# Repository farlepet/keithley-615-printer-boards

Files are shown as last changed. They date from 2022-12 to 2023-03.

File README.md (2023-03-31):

Keithley 615 Electrometer Printer Board Recreation
==================================================

This repo contains modern reproductions of the buffer/printer PCBs (PC209, PC218)
for the Keithley 615 electrometer.

Boards
------

 - PC218
   - Signal inverter/buffer board
   - Recreation of the origional PC218 schematic using modern SMD components is
     in the `PC218` directory
   - A simplified version using more modern ICs can be found in the `PC218v2` directory
 - PC209
   - Signal inverter/buffer and trigger board
   - Simplified version of the origional board can be found in the `PC209` directory
     - Same inverter/buffer scheme as PC218v2, with the origional trigger pulse
       generator and logic reduced down to discrete transistors, to simplify design.
 - Digital Interface Board
   - This will be a new board designed to connect to the 615 via the 50-pin
     Centronics connector
   - Planned features:
     - Passive data collection
     - Active triggering
     - USB-serial
     - RS-232 via DE-9
     - Ethernet

Photos
------

PC218 v2.2:
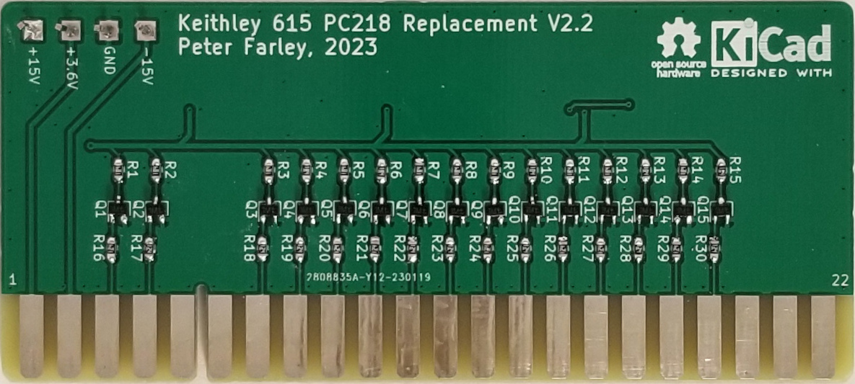
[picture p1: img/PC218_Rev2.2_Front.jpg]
Front of PC218 board v2.2

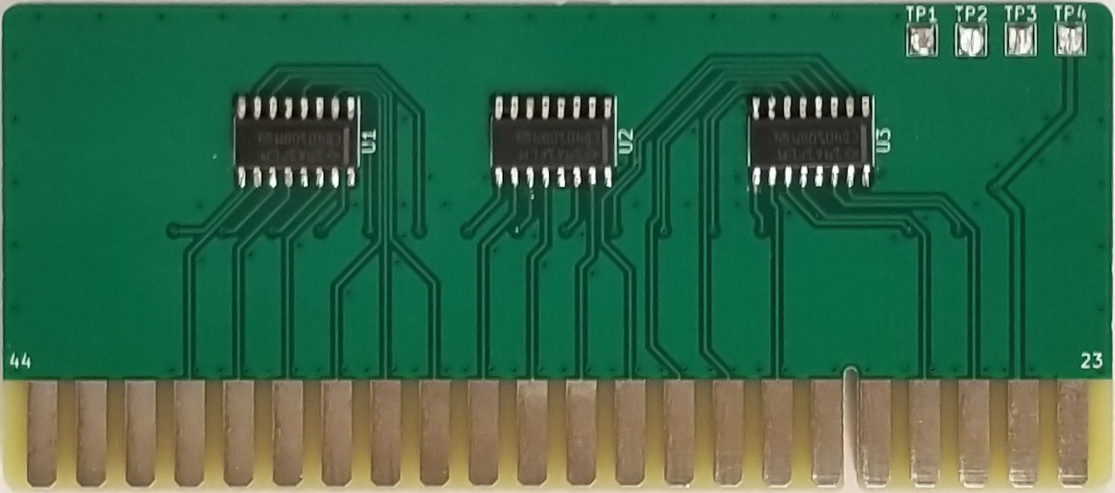
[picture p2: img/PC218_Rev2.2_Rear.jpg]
Rear of PC218 board v2.2


PC209 v1.0:
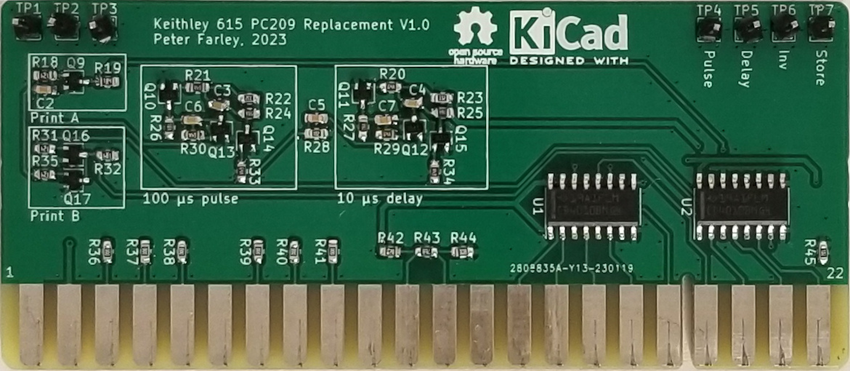
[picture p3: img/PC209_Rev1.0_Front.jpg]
Front of PC209 board v1.0

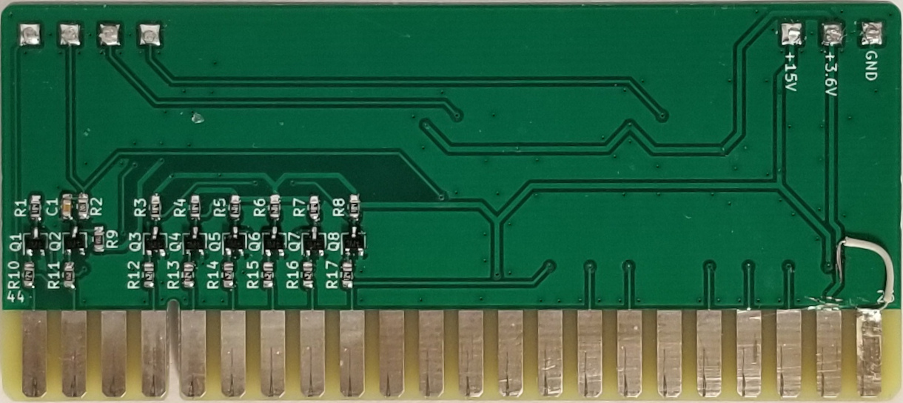
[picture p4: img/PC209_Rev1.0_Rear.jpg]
Rear of PC209 board v1.0


Interface/network board v1.0:
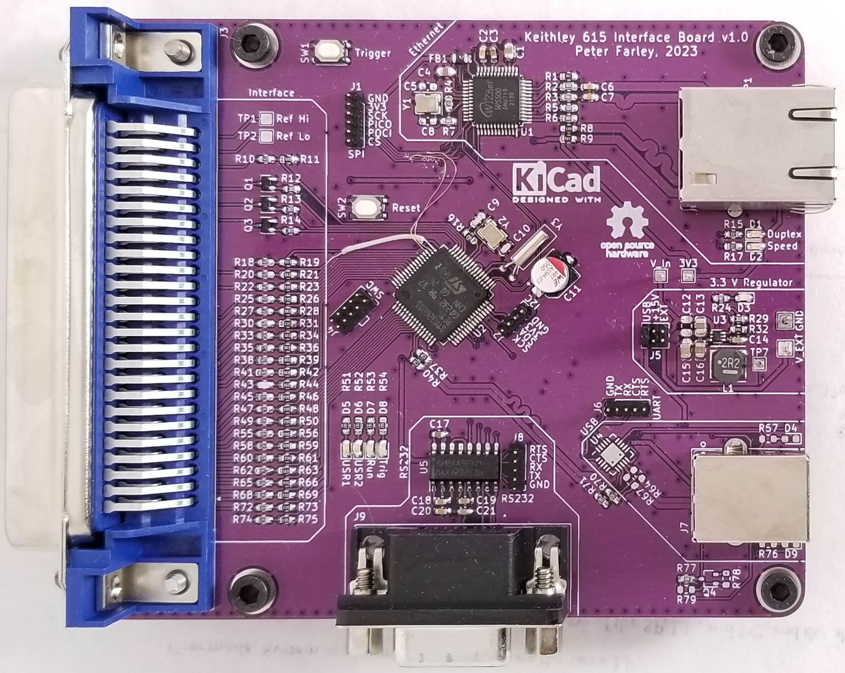
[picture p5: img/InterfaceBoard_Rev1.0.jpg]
Interface board v1.0


50-pin test board v1.0:
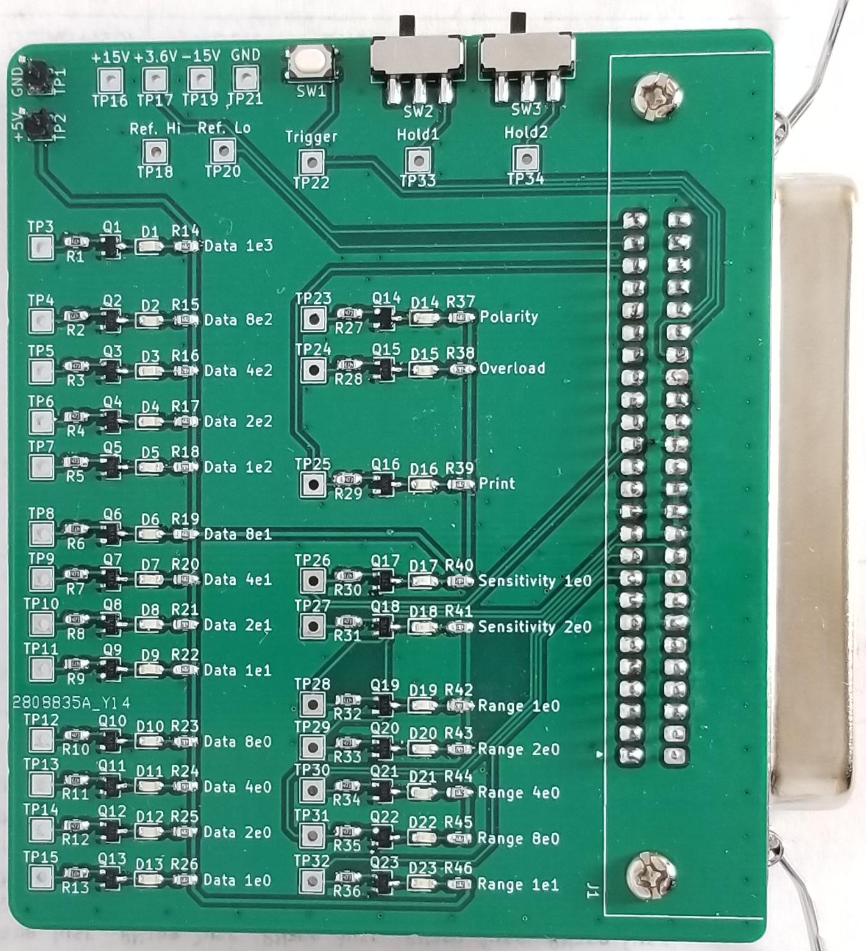
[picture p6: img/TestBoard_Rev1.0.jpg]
50-pin test board v1.0


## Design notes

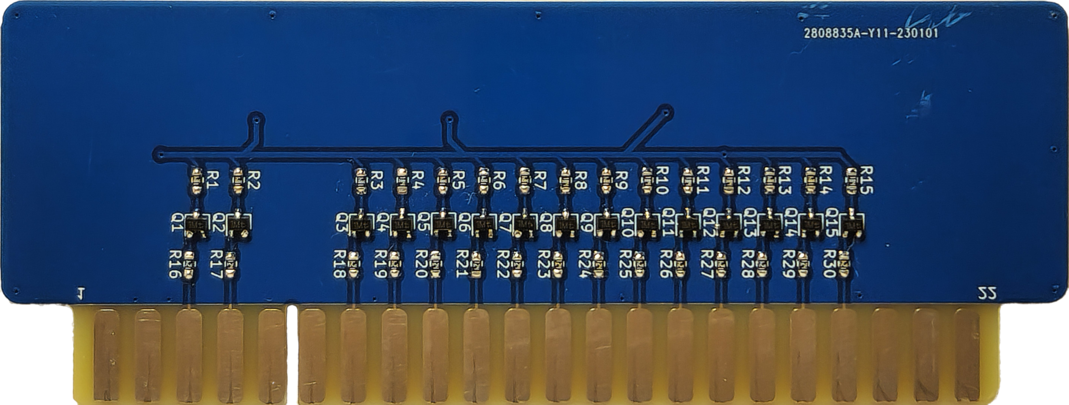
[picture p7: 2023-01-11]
img/PC218_Rev2.0_Front.png

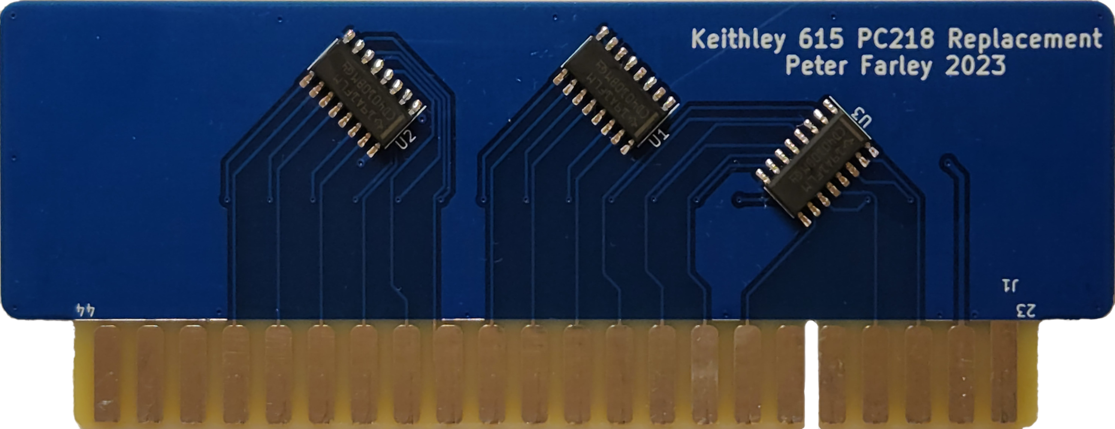
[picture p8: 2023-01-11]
img/PC218_Rev2.0_Rear.png

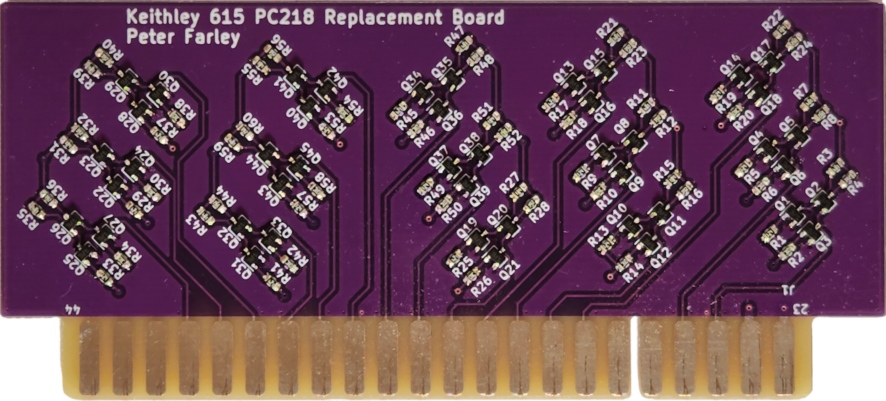
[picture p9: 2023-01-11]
img/PC218_Rev1.0.png

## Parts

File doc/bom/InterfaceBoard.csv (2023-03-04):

Source: | /home/farlepet/projects/electronics/test_equipment/keithley_615_printer_board/InterfaceBoard/InterfaceBoard.kicad_sch
Date: | Sat 04 Mar 2023 08:33:24 AM CST
Tool: | Eeschema (6.0.11)
Generator: | /usr/share/kicad/plugins/bom_csv_grouped_by_value.py
Component Count: | 163
Collated Components:
Item | Qty | Reference(s) | Value | LibPart | Footprint | Datasheet | DigiKey | MANUFACTURER | Model | PART_REV | STANDARD
1 | 4 | C1, C4, C12, C13 | 10uF | Device:C_Small | Capacitor_SMD:C_0805_2012Metric | https://media.digikey.com/pdf/Data%20Sheets/Samsung%20PDFs/CL21A106MQFNNNE_Spec.pdf | https://www.digikey.com/en/products/detail/samsung-electro-mechanics/CL21A106MQFNNNE/3886956
2 | 5 | C2, C5, C8, C36, C37 | 10nF | Device:C_Small | Capacitor_SMD:C_0603_1608Metric | ~ | https://www.digikey.com/en/products/detail/walsin-technology-corporation/0603B103K500CT/9354883
3 | 2 | C3, C35 | 4.7uF | Device:C_Small | Capacitor_SMD:C_0603_1608Metric | ~ | https://www.digikey.com/en/products/detail/samsung-electro-mechanics/CL10A475KQ8NNNC/3886703
4 | 3 | C6, C7, C29 | 6.8nF | Device:C_Small | Capacitor_SMD:C_0603_1608Metric | ~ | https://www.digikey.com/en/products/detail/walsin-technology-corporation/0603B683K160CT/9354958
5 | 2 | C9, C10 | 12pF | Device:C_Small | Capacitor_SMD:C_0603_1608Metric | http://www.passivecomponent.com/wp-content/uploads/datasheet/WTC_MLCC_General_Purpose.pdf | https://www.digikey.com/en/products/detail/walsin-technology-corporation/0603N120J500CT/9354977
6 | 1 | C11 | 4.7uF | Device:C_Polarized_Small | Capacitor_SMD:CP_Elec_5x5.9 | https://www.we-online.com/components/products/datasheet/865230642008.pdf | https://www.digikey.com/en/products/detail/w%C3%BCrth-elektronik/865230642008/5727868
7 | 15 | C14, C18, C19, C20, C21, C22, C23, C24, C25, C26, C27, C28, C32, C33, C34 | 100nF | Device:C_Small | Capacitor_SMD:C_0603_1608Metric | ~ | https://www.digikey.com/en/products/detail/samsung-electro-mechanics/CL10B104KB8NNWC/3887593
8 | 2 | C15, C16 | 22uF | Device:C_Small | Capacitor_SMD:C_0805_2012Metric | https://media.digikey.com/pdf/Data%20Sheets/Samsung%20PDFs/CL21A226MAYNNNE_Spec.pdf | https://www.digikey.com/en/products/detail/samsung-electro-mechanics/CL21A226MAYNNNE/10479857
9 | 1 | C17 | 1uF | Device:C_Small | Capacitor_SMD:C_0603_1608Metric | ~ | https://www.digikey.com/en/products/detail/samsung-electro-mechanics/CL10A105KA8NNNC/3886760
10 | 2 | C30, C31 | 22pF | Device:C_Small | Capacitor_SMD:C_0603_1608Metric | ~ | https://www.digikey.com/en/products/detail/walsin-technology-corporation/0603N220J500CT/9355000
11 | 2 | C38, C39 | 47pF | Device:C_Small | Capacitor_SMD:C_0603_1608Metric | ~ | https://www.digikey.com/en/products/detail/walsin-technology-corporation/0603N470J500CT/9355025
12 | 1 | D1 | Duplex | Device:LED_Small | LED_SMD:LED_0603_1608Metric | ~ | https://www.digikey.com/en/products/detail/harvatek-corporation/B1911USD-20D000114U1930/15519991
13 | 1 | D2 | Speed | Device:LED_Small | LED_SMD:LED_0603_1608Metric | ~ | https://www.digikey.com/en/products/detail/harvatek-corporation/B1911USD-20D000114U1930/15519991
14 | 7 | D3, D4, D5, D6, D7, D8, D9 | Red | Device:LED_Small | LED_SMD:LED_0603_1608Metric | ~ | https://www.digikey.com/en/products/detail/harvatek-corporation/B1911USD-20D000114U1930/15519991
15 | 3 | D10, D11, D12 | PE1605M1Q | Device:D_TVS | Diode_SMD:D_0402_1005Metric | https://www.panjit.com.tw/upload/datasheet/PE1605M1Q.pdf | https://www.digikey.com/en/products/detail/panjit-international-inc/PE1605M1Q-R1-00001/15798503
16 | 1 | FB1 | 1k | Device:FerriteBead_Small | Inductor_SMD:L_0805_2012Metric | https://abracon.com/Magnetics/new/ACML-0805.pdf | https://www.digikey.com/en/products/detail/abracon-llc/ACML-0805-102-T/4696707
17 | 1 | J3 | Keithley_50-Pin_Connector | lib_symbols:Keithley_50-Pin_Connector | lib:NorComp_112-050-213R001 |  | https://www.digikey.com/en/products/detail/norcomp-inc/112-050-213R001/955161
18 | 1 | J5 | Conn_02x03_Odd_Even | Connector_Generic:Conn_02x03_Odd_Even | Connector_PinHeader_1.27mm:PinHeader_2x03_P1.27mm_Vertical | ~
19 | 1 | J7 | USB_B | lib_symbols:UJ2-BH-W1-TH | lib:CUI_UJ2-BH-W1-TH | https://www.cuidevices.com/product/resource/uj2-bh-th.pdf | https://www.digikey.com/en/products/detail/cui-devices/UJ2-BH-W1-TH/6188082 | CUI INC |  | 1.0 | MANUFACTURER RECOMENDATION
20 | 1 | J9 | DB9_Female_MountingHoles | Connector:DB9_Female_MountingHoles | lib:ASSMANN_A-DF_09_A_KG-T2S | http://www.assmann-wsw.com/uploads/datasheets/ASS_4888_CO.pdf | https://www.digikey.com/en/products/detail/assmann-wsw-components/A-DF-09-A-KG-T2S/1241800
21 | 1 | L1 | 2.2 uH | Device:L_Small | Inductor_SMD:L_Taiyo-Yuden_NR-50xx | https://media.digikey.com/pdf/Data%20Sheets/Taiyo%20Yuden%20PDFs%20URL%20links/NRS5024T2R2NMGJ_SS.pdf | https://www.digikey.com/en/products/detail/taiyo-yuden/NRS5024T2R2NMGJ/4970841
22 | 1 | P1 | RB1-125BAG1A | lib_symbols:RB1-125BAG1A | lib:WIZNET_RB1-125BAG1A |  | https://www.digikey.com/en/products/detail/wiznet/RB1-125BAG1A/3829637 | WIZnet
23 | 3 | Q1, Q2, Q3 | BC848W | Transistor_BJT:BC848W | Package_TO_SOT_SMD:SOT-323_SC-70 | http://www.infineon.com/dgdl/Infineon-BC847SERIES_BC848SERIES_BC849SERIES_BC850SERIES-DS-v01_01-en.pdf?fileId=db3a304314dca389011541d4630a1657
24 | 1 | Q4 | BC856W | Transistor_BJT:BC856W | Package_TO_SOT_SMD:SOT-323_SC-70 | https://www.onsemi.com/pub/Collateral/BC860-D.pdf
25 | 1 | R1 | 12.4k | Device:R_Small | Resistor_SMD:R_0603_1608Metric | ~ | https://www.digikey.com/en/products/detail/stackpole-electronics-inc/RMCF0603FT12K4/1761222
26 | 13 | R2, R3, R5, R6, R7, R70, R71, R77, R80, R86, R87, R90, R91 | 0 | Device:R_Small | Resistor_SMD:R_0603_1608Metric | ~ | https://www.digikey.com/en/products/detail/walsin-technology-corporation/WR06X000-PTL/5978108
27 | 1 | R4 | 1M | Device:R_Small | Resistor_SMD:R_0603_1608Metric | ~ | https://www.digikey.com/en/products/detail/walsin-technology-corporation/WR06X105-JTL/13239221
28 | 4 | R8, R9, R82, R83 | 49.9 | Device:R_Small | Resistor_SMD:R_0603_1608Metric | ~ | https://www.digikey.com/en/products/detail/stackpole-electronics-inc/RMCF0603FT49R9/1760879
29 | 23 | R10, R18, R20, R22, R25, R27, R30, R33, R35, R38, R41, R43, R45, R47, R49, R55, R58, R60, R62, R65, R68, R72, R74 | 220k | Device:R_Small | Resistor_SMD:R_0603_1608Metric | ~ | https://www.digikey.com/en/products/detail/walsin-technology-corporation/WR06X224-JTL/13238727
30 | 23 | R11, R19, R21, R23, R26, R28, R31, R34, R36, R39, R42, R44, R46, R48, R50, R56, R59, R61, R63, R66, R69, R73, R75 | 56k | Device:R_Small | Resistor_SMD:R_0603_1608Metric | ~ | https://www.digikey.com/en/products/detail/stackpole-electronics-inc/RMCF0603JT56K0/1757988
31 | 5 | R12, R13, R14, R29, R79 | 10k | Device:R_Small | Resistor_SMD:R_0603_1608Metric | ~ | https://www.digikey.com/en/products/detail/yageo/RC0603FR-1010KL/12756395
32 | 4 | R15, R17, R81, R84 | 330 | Device:R_Small | Resistor_SMD:R_0603_1608Metric | ~ | https://www.digikey.com/en/products/detail/walsin-technology-corporation/WR06X331-JTL/13240667
33 | 1 | R16 | 1.6k | Device:R_Small | Resistor_SMD:R_0603_1608Metric | ~ | https://www.digikey.com/en/products/detail/stackpole-electronics-inc/RMCF0603FT1K60/1761204
34 | 3 | R24, R57, R76 | 1k | Device:R_Small | Resistor_SMD:R_0603_1608Metric | ~ | https://www.digikey.com/en/products/detail/walsin-technology-corporation/WR06X102-JTL/13241138
35 | 1 | R32 | 31.6k | Device:R_Small | Resistor_SMD:R_0603_1608Metric | ~ | https://www.digikey.com/en/products/detail/bourns-inc/CR0603-FX-3162ELF/3783940
36 | 4 | R37, R40, R64, R67 | 27 | Device:R_Small | Resistor_SMD:R_0603_1608Metric | ~ | https://www.digikey.com/en/products/detail/stackpole-electronics-inc/RMCF0603FT27R0/1760818
37 | 4 | R51, R52, R53, R54 | 1.8k | Device:R_Small | Resistor_SMD:R_0603_1608Metric | ~ | https://www.digikey.com/en/products/detail/stackpole-electronics-inc/RMCF0603JG1K80/1712125
38 | 1 | R78 | 180k | Device:R_Small | Resistor_SMD:R_0603_1608Metric | ~ | https://www.digikey.com/en/products/detail/yageo/RC0603FR-10180KL/14008354
39 | 1 | R85 | 10 | Device:R_Small | Resistor_SMD:R_0603_1608Metric | ~ | https://www.digikey.com/en/products/detail/walsin-technology-corporation/WR06X10R0FTL/13238870
40 | 2 | R88, R89 | 1.5k | Device:R_Small | Resistor_SMD:R_0603_1608Metric | ~ | https://www.digikey.com/en/products/detail/walsin-technology-corporation/WR06X1501FTL/13239261
41 | 2 | SW1, SW2 | PTS810 | Switch:SW_Push | Button_Switch_SMD:SW_SPST_PTS810 | ~ | https://www.digikey.com/en/products/detail/c-k/PTS810-SJK-250-SMTR-LFS/4176611
42 | 1 | U1 | W5500 | Interface_Ethernet:W5500 | Package_QFP:LQFP-48_7x7mm_P0.5mm | http://wizwiki.net/wiki/lib/exe/fetch.php/products:w5500:w5500_ds_v109e.pdf | https://www.digikey.com/en/products/detail/wiznet/W5500/4425702
43 | 1 | U2 | STM32G0B1RET | lib_symbols:STM32G0B1RET | Package_QFP:LQFP-64_10x10mm_P0.5mm |  | https://www.digikey.com/en/products/detail/stmicroelectronics/STM32G0B1RET6/13693663
44 | 1 | U3 | AP62250Z6 | Regulator_Switching:AP62250Z6 | Package_TO_SOT_SMD:SOT-563 | https://www.diodes.com/assets/Datasheets/AP62250.pdf | https://www.digikey.com/en/products/detail/diodes-incorporated/AP62250Z6-7/12349310
45 | 1 | U4 | FT231XQ | Interface_USB:FT231XQ | Package_DFN_QFN:QFN-20-1EP_4x4mm_P0.5mm_EP2.5x2.5mm | https://www.ftdichip.com/Support/Documents/DataSheets/ICs/DS_FT231X.pdf | https://www.digikey.com/en/products/detail/ftdi-future-technology-devices-international-ltd/FT231XQ-T/3749470
46 | 1 | U5 | MAX3232 | Interface_UART:MAX3232 | Package_SO:SOIC-16_3.9x9.9mm_P1.27mm | https://www.ti.com/lit/ds/symlink/max3232e.pdf | https://www.digikey.com/en/products/detail/texas-instruments/MAX3232EIDR/1089416?s=N4IgTCBcDaILYEMDGBmMaQF0C%2BQ
47 | 1 | Y1 | 25 MHz | Device:Crystal_GND24 | Crystal:Crystal_SMD_3225-4Pin_3.2x2.5mm | ~ | https://www.digikey.com/en/products/detail/raltron-electronics/RH100-25-000-18-F-TR/15963302 |  | RH100-25.000-18-F-TR
48 | 1 | Y2 | 24 MHz | Device:Crystal_GND24_Small | Crystal:Crystal_SMD_3225-4Pin_3.2x2.5mm | https://www.raltron.com/webproducts/specs/CRYSTAL/RH100-24.000-12-1010-EXT-TR.pdf | https://www.digikey.com/en/products/detail/raltron-electronics/RH100-24-000-12-1010-EXT-TR/15963325
49 | 1 | Y3 | 32.768 kHz | Device:Crystal_Small | Crystal:Crystal_C26-LF_D2.1mm_L6.5mm_Horizontal | https://www.yic.com.tw/wp-content/uploads/2019/05/YIC-DT38-DT26-DT15.pdf | https://www.digikey.com/en/products/detail/yic/32-768K12-5P2-DT26/15648604

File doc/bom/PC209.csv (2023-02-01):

Source: | /home/farlepet/projects/electronics/test_equipment/keithley_615_printer_board/PC209/PC209.kicad_sch
Date: | Wed 01 Feb 2023 06:48:42 AM CST
Tool: | Eeschema (6.0.11)
Generator: | /usr/share/kicad/plugins/bom_csv_grouped_by_value.py
Component Count: | 72
Collated Components:
Item | Qty | Reference(s) | Value | LibPart | Footprint | Datasheet | Digikey
1 | 2 | C1, C5 | 1 nF | Device:C_Small | Capacitor_SMD:C_0603_1608Metric | ~ | https://www.digikey.com/en/products/detail/walsin-technology-corporation/0603B102K500CT/9354877
2 | 1 | C2 | 100 pF | Device:C_Small | Capacitor_SMD:C_0603_1608Metric | ~ | https://www.digikey.com/en/products/detail/walsin-technology-corporation/0603B101K500CT/14836835
3 | 1 | C3 | 100 nF | Device:C_Small | Capacitor_SMD:C_0603_1608Metric | ~ | https://www.digikey.com/en/products/detail/samsung-electro-mechanics/CL10B104KB8NNWC/3887593
4 | 1 | C4 | 3.3 nF | Device:C_Small | Capacitor_SMD:C_0603_1608Metric | ~ | https://www.digikey.com/en/products/detail/samsung-electro-mechanics/CL10B332KB8NNNC/3887416
5 | 2 | C6, C7 | 470 pF | Device:C_Small | Capacitor_SMD:C_0603_1608Metric | ~ | https://www.digikey.com/en/products/detail/samsung-electro-mechanics/CL10B471KB8NNNC/3886752
6 | 1 | J1 | PC209_BoardEdge_44pin | lib_symbols:PC209_BoardEdge_44pin | footprints:PC209_Edge_Connector
7 | 17 | Q1, Q2, Q3, Q4, Q5, Q6, Q7, Q8, Q9, Q10, Q11, Q12, Q13, Q14, Q15, Q16, Q17 | BC848W | Transistor_BJT:BC848W | Package_TO_SOT_SMD:SOT-323_SC-70 | http://www.infineon.com/dgdl/Infineon-BC847SERIES_BC848SERIES_BC849SERIES_BC850SERIES-DS-v01_01-en.pdf?fileId=db3a304314dca389011541d4630a1657 | https://www.digikey.com/en/products/detail/nexperia-usa-inc/BC848W-115/1232299
8 | 9 | R1, R3, R4, R5, R6, R7, R8, R19, R32 | 180k | Device:R_Small | Resistor_SMD:R_0603_1608Metric | ~ | https://www.digikey.com/en/products/detail/yageo/RC0603FR-10180KL/14008354
9 | 3 | R2, R28, R45 | 1k | Device:R_Small | Resistor_SMD:R_0603_1608Metric | ~ | https://www.digikey.com/en/products/detail/walsin-technology-corporation/WR06X102-JTL/13241138
10 | 5 | R9, R24, R25, R26, R27 | 634 | Device:R_Small | Resistor_SMD:R_0603_1608Metric | ~ | https://www.digikey.com/en/products/detail/stackpole-electronics-inc/RMCF0603FT634R/1760903
11 | 10 | R10, R12, R13, R14, R15, R16, R17, R18, R31, R35 | 120k | Device:R_Small | Resistor_SMD:R_0603_1608Metric | ~ | https://www.digikey.com/en/products/detail/yageo/RC0603FR-13120KL/14008276
12 | 7 | R11, R20, R21, R29, R30, R33, R34 | 453 | Device:R_Small | Resistor_SMD:R_0603_1608Metric | ~ | https://www.digikey.com/en/products/detail/stackpole-electronics-inc/RMCF0603FT453R/1714054
13 | 2 | R22, R23 | 3.3k | Device:R_Small | Resistor_SMD:R_0603_1608Metric | ~ | https://www.digikey.com/en/products/detail/walsin-technology-corporation/WR06X3301FTL/13239039
14 | 6 | R36, R37, R38, R39, R40, R41 | 0 | Device:R_Small | Resistor_SMD:R_0603_1608Metric | ~ | https://www.digikey.com/en/products/detail/walsin-technology-corporation/WR06X000-PTL/5978108
15 | 1 | R42 | 6.98k | Device:R | Resistor_SMD:R_0603_1608Metric | ~ | https://www.digikey.com/en/products/detail/yageo/RC0603FR-076K98L/727326
16 | 1 | R43 | 6.04k | Device:R | Resistor_SMD:R_0603_1608Metric | ~ | https://www.digikey.com/en/products/detail/yageo/RC0603FR-076K04L/727317
17 | 1 | R44 | 2k | Device:R | Resistor_SMD:R_0603_1608Metric | ~ | https://www.digikey.com/en/products/detail/yageo/RC0603FR-072KL/727009
18 | 2 | U1, U2 | 4010 | 4xxx:4010 | Package_SO:SOIC-16_3.9x9.9mm_P1.27mm | http://www.ti.com/lit/ds/symlink/cd4010b-q1.pdf | https://www.digikey.com/en/products/detail/texas-instruments/CD4010BM96/1690674

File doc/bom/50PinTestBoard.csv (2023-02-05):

Source: | /home/farlepet/projects/electronics/test_equipment/keithley_615_printer_board/50PinTestBoard/50PinTestBoard.kicad_sch
Date: | Sat 04 Feb 2023 09:08:30 PM CST
Tool: | Eeschema (6.0.11)
Generator: | /usr/share/kicad/plugins/bom_csv_grouped_by_value.py
Component Count: | 98
Item | Qty | Reference(s) | Value | LibPart | Footprint | Datasheet | DigiKey
1 | 23 | D1, D2, D3, D4, D5, D6, D7, D8, D9, D10, D11, D12, D13, D14, D15, D16, D17, D18, D19, D20, D21, D22, D23 | LED | Device:LED | LED_SMD:LED_0603_1608Metric | ~ | https://www.digikey.com/en/products/detail/harvatek-corporation/B1911NG-20D000214U1930/15519989
2 | 1 | J1 | Keithley_50-Pin_Connector | lib_symbols:Keithley_50-Pin_Connector | footprints:NorComp_112-050-213R001 |  | https://www.digikey.com/en/products/detail/norcomp-inc/112-050-213R001/955161
3 | 23 | Q1, Q2, Q3, Q4, Q5, Q6, Q7, Q8, Q9, Q10, Q11, Q12, Q13, Q14, Q15, Q16, Q17, Q18, Q19, Q20, Q21, Q22, Q23 | BC848W | Transistor_BJT:BC848W | Package_TO_SOT_SMD:SOT-323_SC-70 | http://www.infineon.com/dgdl/Infineon-BC847SERIES_BC848SERIES_BC849SERIES_BC850SERIES-DS-v01_01-en.pdf?fileId=db3a304314dca389011541d4630a1657 | https://www.digikey.com/en/products/detail/nexperia-usa-inc/BC848W-115/1232299
4 | 23 | R1, R2, R3, R4, R5, R6, R7, R8, R9, R10, R11, R12, R13, R27, R28, R29, R30, R31, R32, R33, R34, R35, R36 | 50k | Device:R_Small | Resistor_SMD:R_0603_1608Metric | ~ | https://www.digikey.com/en/products/detail/walsin-technology-corporation/WR06X473-JTL/13240660
5 | 23 | R14, R15, R16, R17, R18, R19, R20, R21, R22, R23, R24, R25, R26, R37, R38, R39, R40, R41, R42, R43, R44, R45, R46 | 6.8k | Device:R_Small | Resistor_SMD:R_0603_1608Metric | ~ | https://www.digikey.com/en/products/detail/walsin-technology-corporation/WR06X682-JTL/13240888
6 | 2 | R47, R48 | 0 | Device:R_Small | Resistor_SMD:R_0603_1608Metric | ~ | https://www.digikey.com/en/products/detail/walsin-technology-corporation/WR06X000-PTL/5978108
7 | 1 | SW1 | SW_Push | Switch:SW_Push | Button_Switch_SMD:SW_SPST_PTS810 | ~ | https://www.digikey.com/en/products/detail/c-k/PTS810-SJK-250-SMTR-LFS/4176611
8 | 2 | SW2, SW3 | SW_SPST | Switch:SW_SPST | Button_Switch_SMD:SW_SPDT_CK-JS102011SAQN | ~ | https://www.digikey.com/en/products/detail/c-k/JS102011SAQN/1640095

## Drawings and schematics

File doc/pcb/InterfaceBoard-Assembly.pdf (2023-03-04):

1 | 2 | 3 | 4 | 5 | 6

A

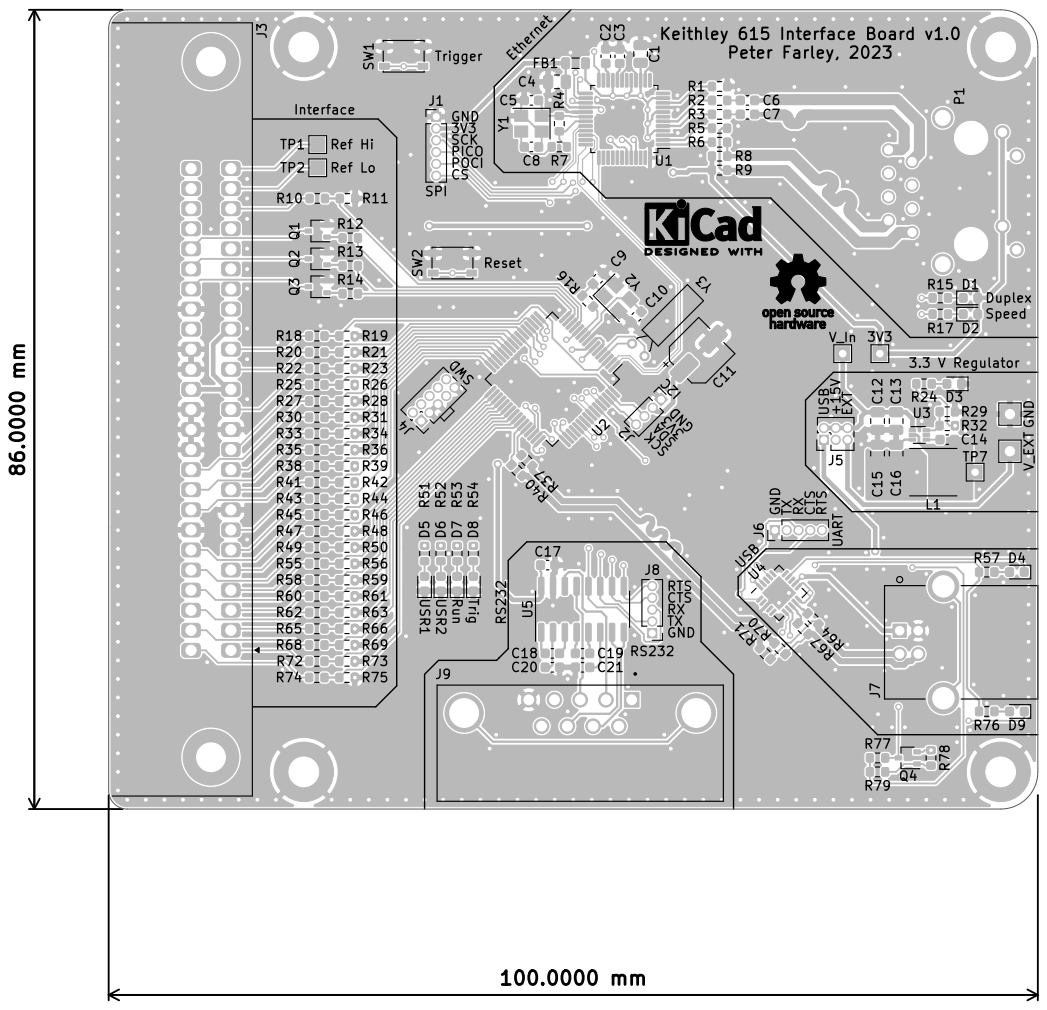
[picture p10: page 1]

Id: 1/1 Title: Keithley 615 Interface Board

1 | 2 | 3 | 4 | 5 | 6

A

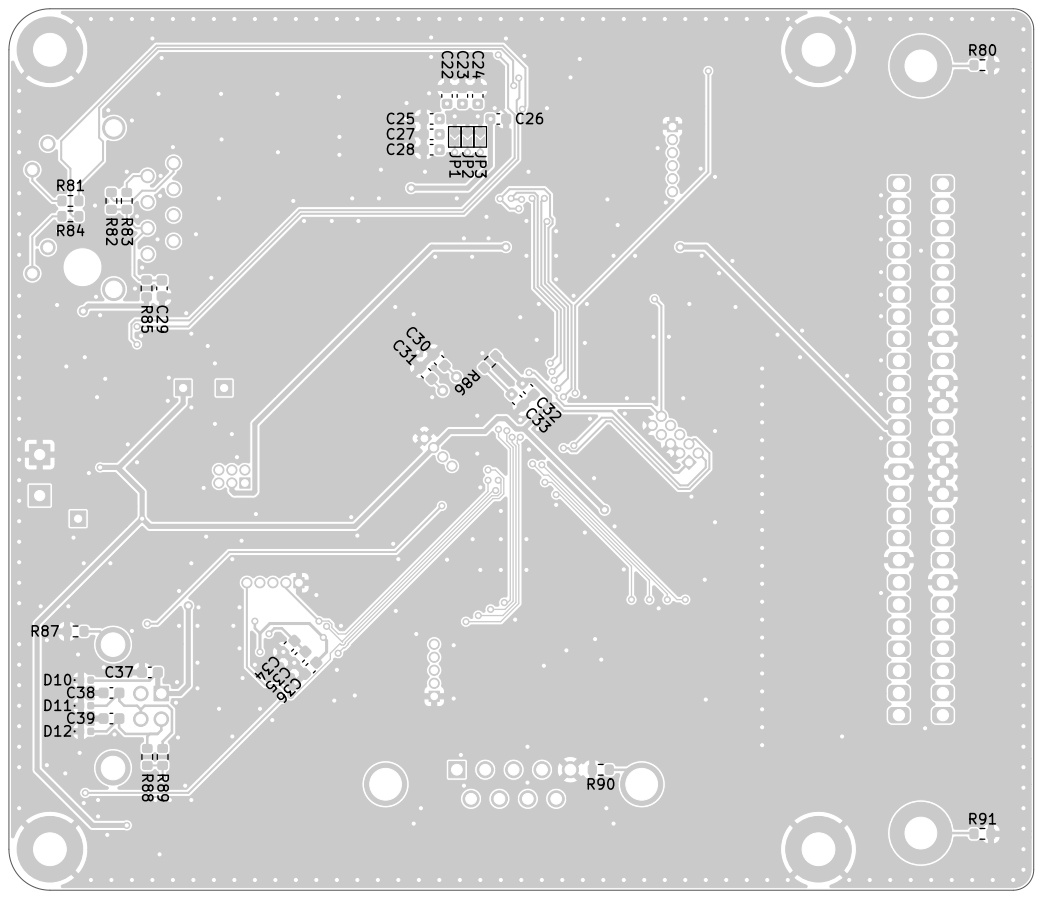
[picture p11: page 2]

Id: 1/1 Title: Keithley 615 Interface Board

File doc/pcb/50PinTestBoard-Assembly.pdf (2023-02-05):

1 | 2 | 3

A

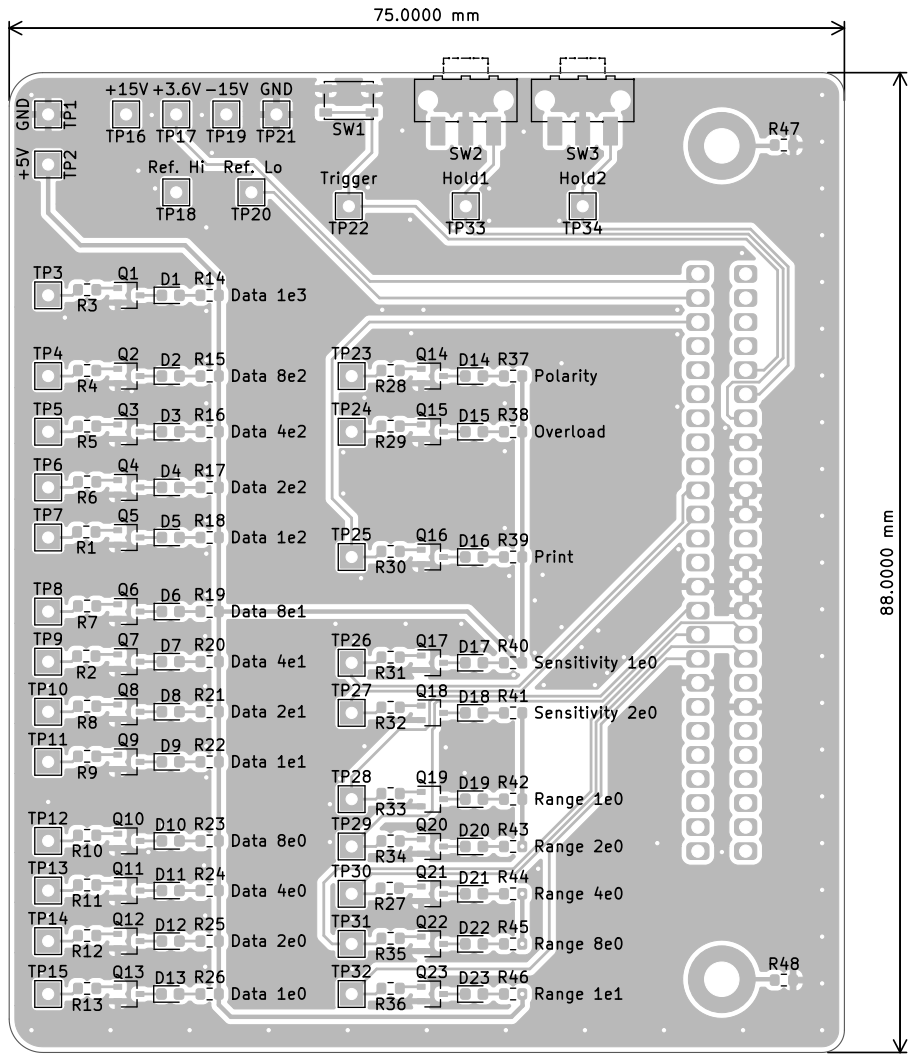
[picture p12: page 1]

1 | 2 | 3

A

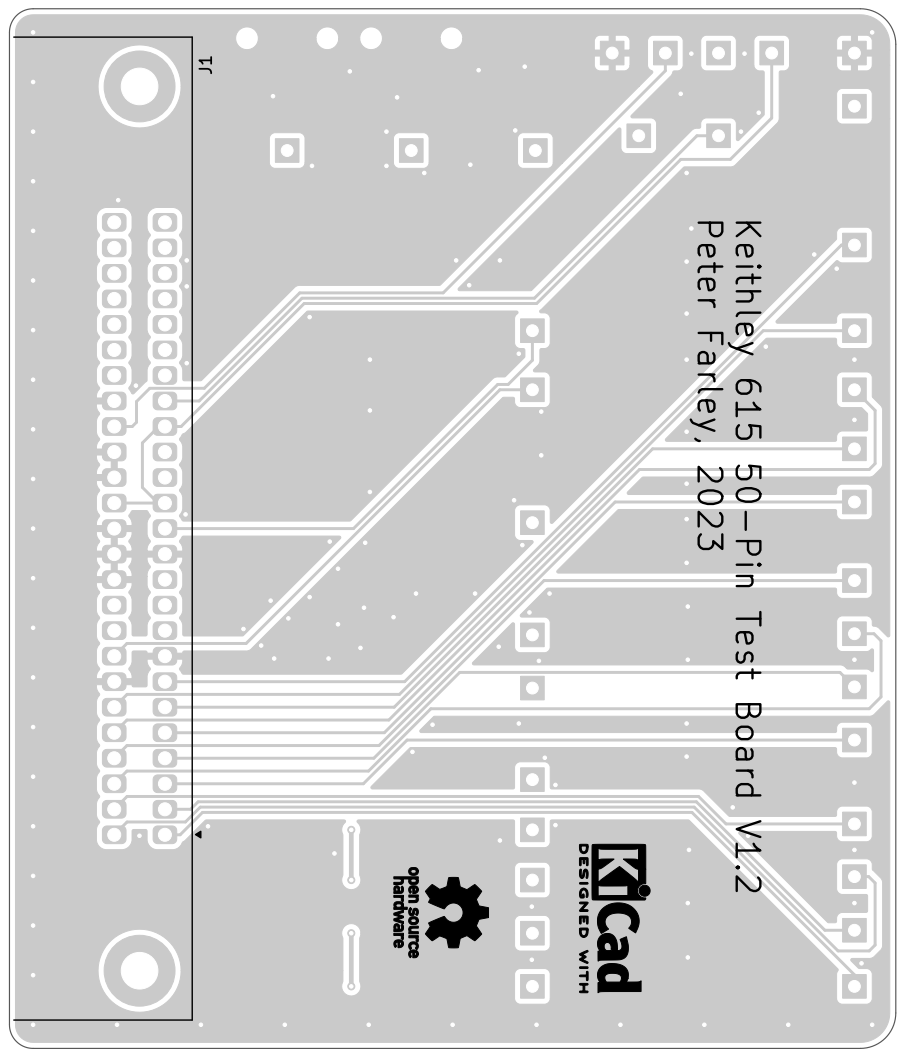
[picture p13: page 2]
D Date: 2023-02-04 KiCad; kicad; (6.0.11) Size: A5; Rev: 1.2; Id: 1/1 Title: Keithley 615 50-Pin; Test Board; Peter Farley Rev 1.0:; Initial Design Rev 1.1: Update connector; footprint Rev1.2:; Fix connector; orientation/pin; numbering; Keithley 615 50-Pin Test Board V1.2 Peter Farley, 2023 J1

File: 50PinTestBoard.kicad_pcb Sheet: BlackAndWhiteBottom

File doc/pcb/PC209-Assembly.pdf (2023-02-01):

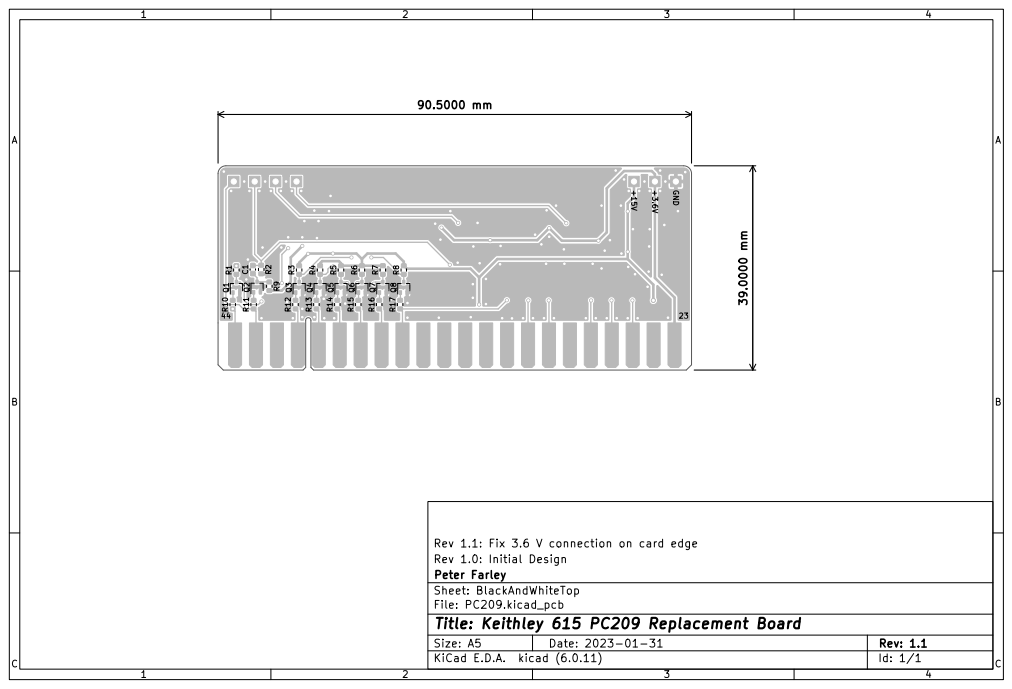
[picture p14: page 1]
BC Date: 2023-01-31 KiCad; kicad; (6.0.11) Size: A5; Rev: 1.1; File: PC209.kicad_pcb Sheet: BlackAndWhiteTop Peter; Farley Rev 1.0:; Initial Design Rev 1.1:; Fix 3.6 V connection; on card edge ⁺¹⁵V; GND R²; R¹²; R¹³ R⁹; R⁴ R¹¹; R¹⁴; R⁸ Q⁷ R¹⁵ Q²; R⁵ R¹⁰; R¹⁷ C¹; R¹⁶ R¹

Id: 1/1 Title: Keithley 615 PC209 Replacement Board

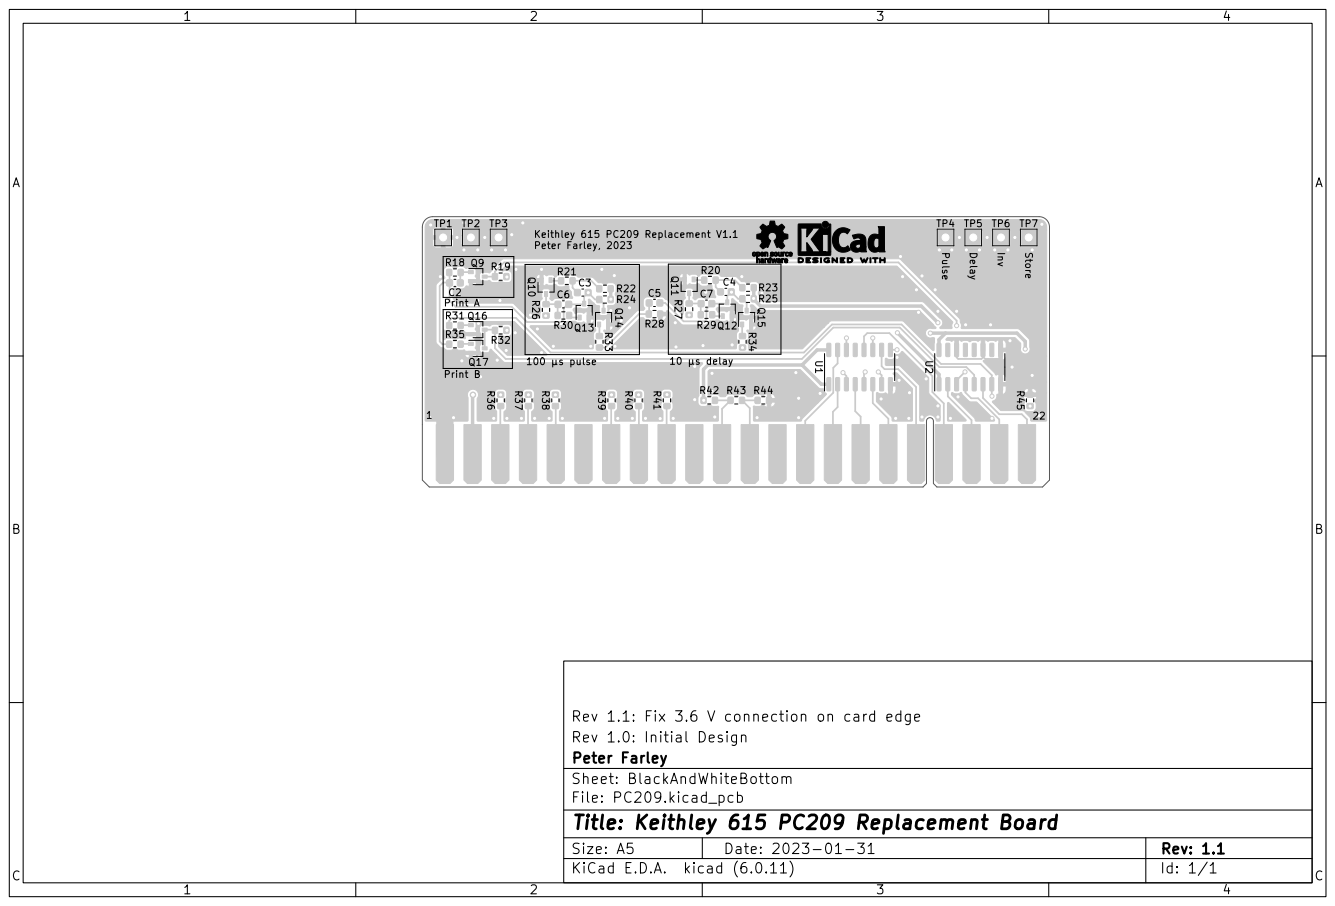
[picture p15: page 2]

Keithley 615 PC209 Replacement V1.1 Peter Farley, 2023

File: PC209.kicad_pcb Sheet: BlackAndWhiteBottom
Id: 1/1 Title: Keithley 615 PC209 Replacement Board

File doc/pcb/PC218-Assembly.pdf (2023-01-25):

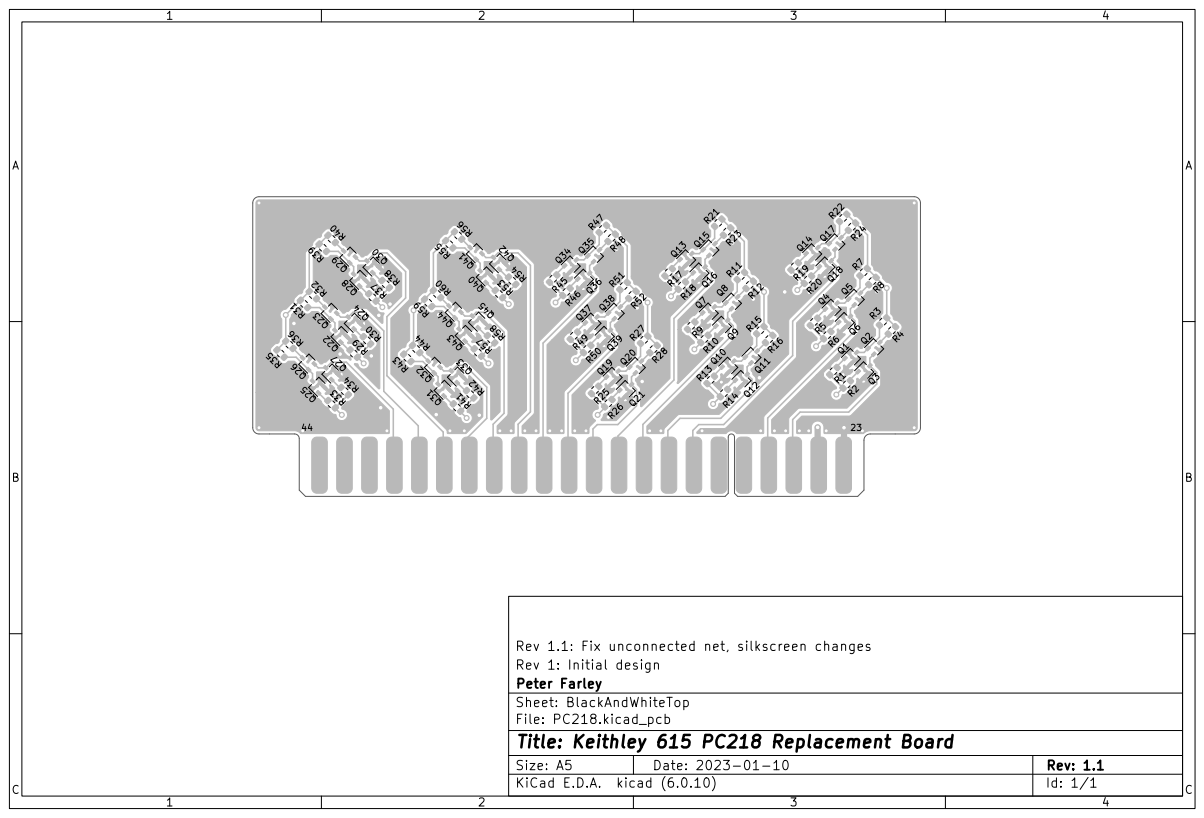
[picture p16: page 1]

Rev 1.1: Fix unconnected net, silkscreen changes
Rev 1: Initial design
Peter Farley
Sheet: BlackAndWhiteTop
File: PC218.kicad_pcb
Id: 1/1 Title: Keithley 615 PC218 Replacement Board

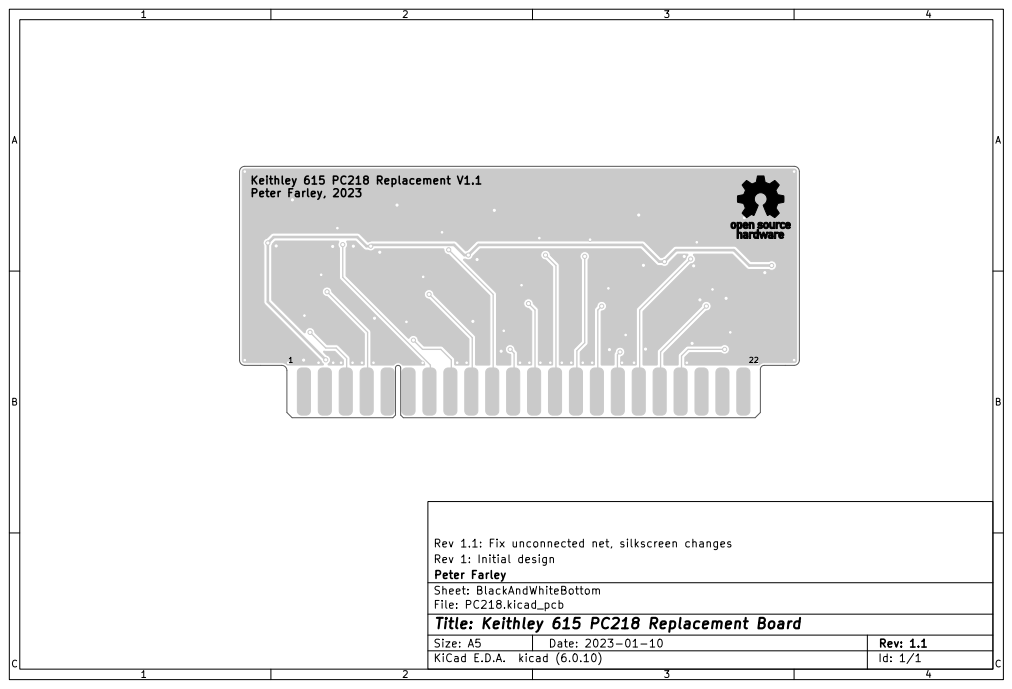
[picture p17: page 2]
BC Date: 2023-01-10 KiCad E.D.A. kicad (6.0.10) Size: A5; Rev: 1.1; Keithley 615 PC218 Replacement V1.1 Peter Farley, 2023

Rev 1.1: Fix unconnected net, silkscreen changes
Rev 1: Initial design
Peter Farley
File: PC218.kicad_pcb Sheet: BlackAndWhiteBottom
Id: 1/1 Title: Keithley 615 PC218 Replacement Board

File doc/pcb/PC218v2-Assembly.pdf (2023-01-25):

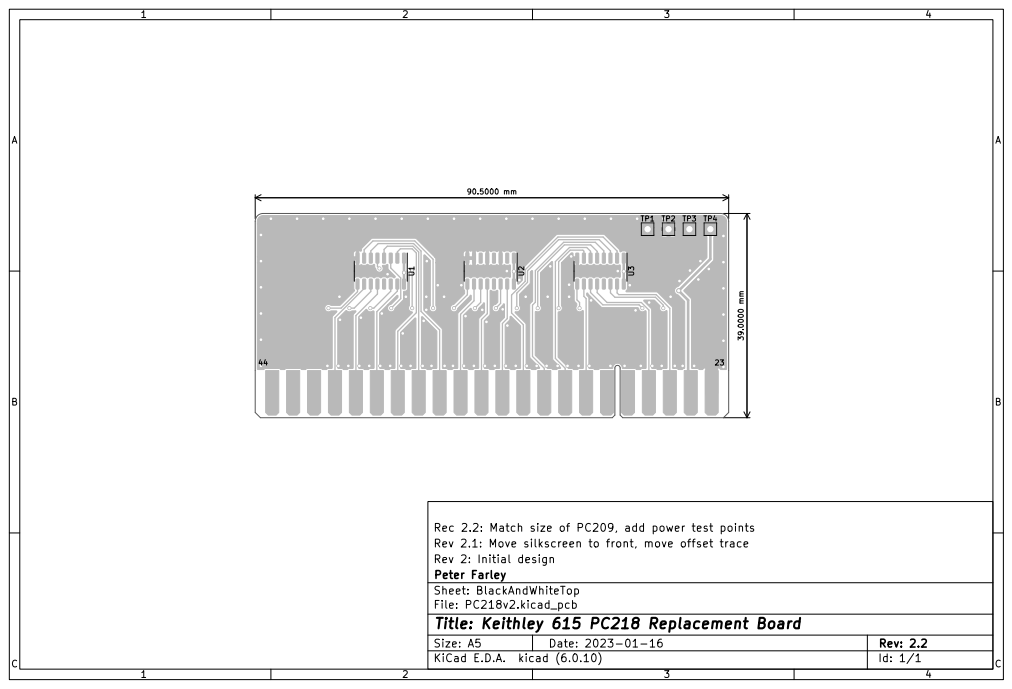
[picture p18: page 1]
BC Date: 2023-01-16 KiCad E.D.A. kicad (6.0.10) Size: A5; Rev: 2.2

Rec 2.2: Match size of PC209, add power test points
Rev 2.1: Move silkscreen to front, move offset trace
Rev 2: Initial design
Peter Farley
Sheet: BlackAndWhiteTop
File: PC218v2.kicad_pcb
Id: 1/1 Title: Keithley 615 PC218 Replacement Board

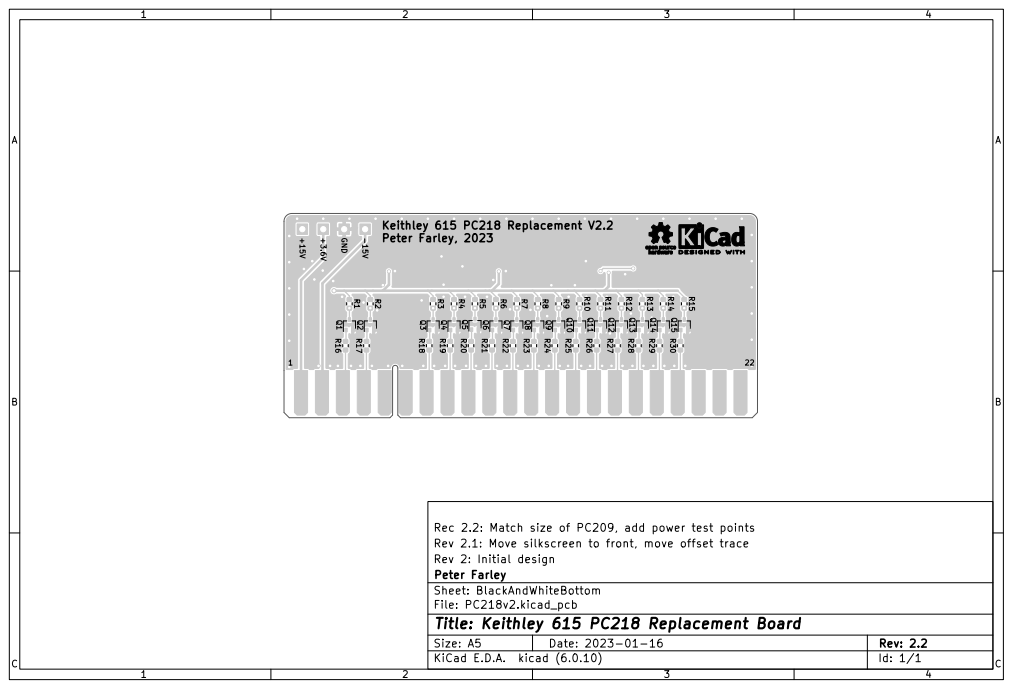
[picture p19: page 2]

Rev 2.1: Move silkscreen to front, move offset trace
Rev 2: Initial design
Peter Farley
File: PC218v2.kicad_pcb Sheet: BlackAndWhiteBottom
Id: 1/1 Title: Keithley 615 PC218 Replacement Board

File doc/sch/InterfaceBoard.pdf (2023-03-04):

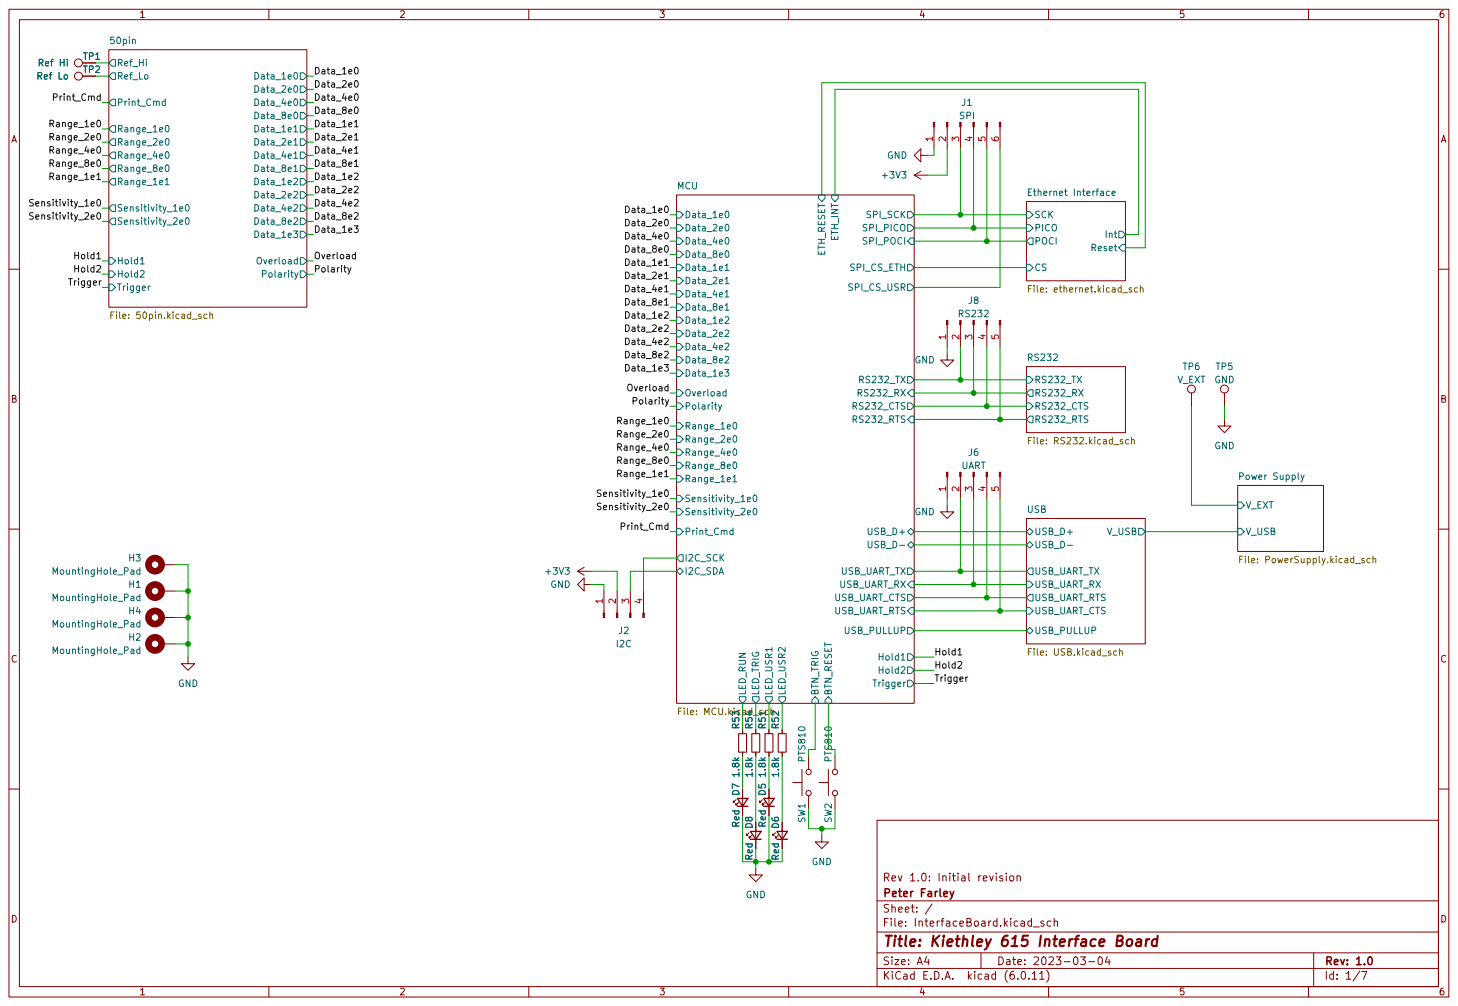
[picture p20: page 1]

Power Supply File: PowerSupply.kicad_sch SPI_PICO
SPI_POCI SPI_CS_ETH

Id: 1/7 Title: Kiethley 615 Interface Board

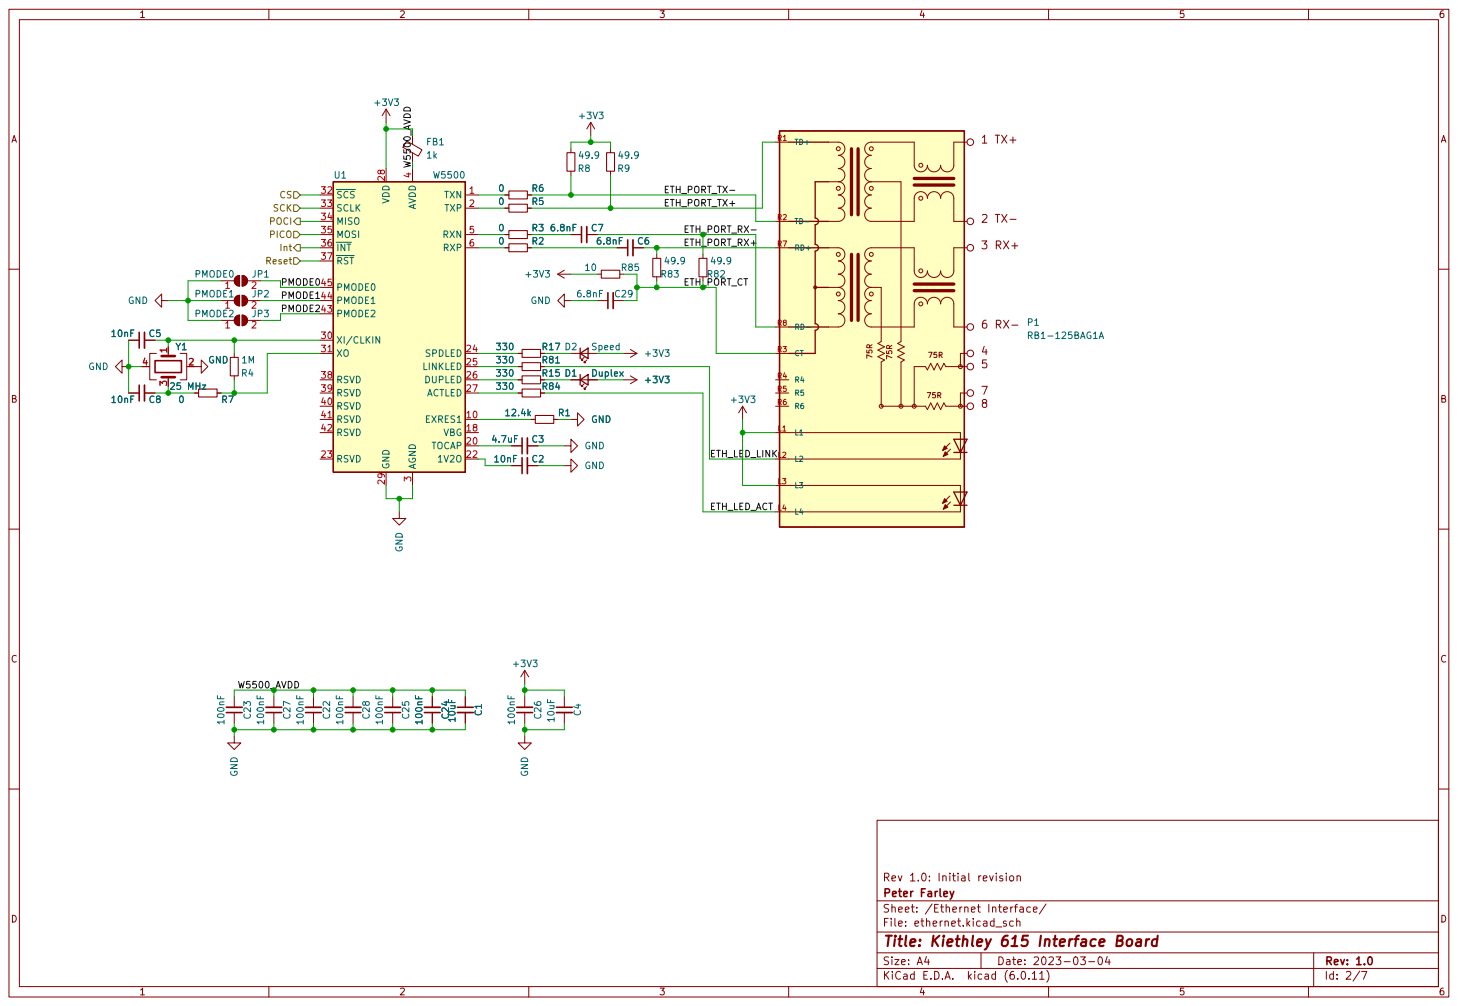
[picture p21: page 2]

4 RSVD 40 RSVD 41 RSVD 42 PMODE2 43 PMODE1 44 PMODE0 45 RXN

3 XI/CLKIN 30 XO 31 ~{SCS} 32 SCLK 33 MISO 34 MOSI 35 ~{INT} 36 ~{RST} 37 RSVD 38 RSVD 39 AVDD

L2
L2 L3 L3

Id: 2/7 Title: Kiethley 615 Interface Board


Id: 3/7 Title: Kiethley 615 Interface Board


17 ~{DTR}18 ~{RTS}19 ~{RI}2 VCCIO 20 GND 21 GND

FTDI USB UART Only populate one DNP for FTDI

3 ~{DSR}4 ~{DCD}5 ~{CTS}6 CBUS2 7 USBDP 8 USBDM 9 U4 FT231XQ D9 Red R76 1k R57 1k

3 GND
4 SHIELD

Id: 4/7 Title: Kiethley 615 Interface Board


Id: 5/7 Title: Kiethley 615 Interface Board


Id: 6/7 Title: Kiethley 615 Interface Board


Input cap current requirements: 5 V: ~150 mA

Id: 7/7 Title: Kiethley 615 Interface Board

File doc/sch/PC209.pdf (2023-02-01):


Hold 2 Out Range Hold Out Hold 1 Out Zero Check Out Buffer Storage

Range Hold Range Signal 8 V

Low Reference Range Hold Out Range 4

Id: 1/2 Title: Keithley 615 PC209 Replacement Board


2 3 Q13 BC848W C7 470 pF GND C6 470 pF TP4 100 þÿ¼spulse R28 1k GND

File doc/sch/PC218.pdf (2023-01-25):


2x10^1 Print 1x10^1 Print 8x10^1 Print 8x10^0 Print 2x10^1

Rev 1: Initial design
File: PC218.kicad_sch Sheet: / Peter Farley

Id: 1/1 Title: Keithley 615 PC218 Replacement Board

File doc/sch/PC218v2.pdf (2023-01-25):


2x10^1 Print 1x10^1 Print Polarity
4x10^0 Print 4x10^1 Print 8x10^1 Print 8x10^0 Print 1x10^3 Overload

Polarity Print 1x10^3 Print 2x10^2 Print 2x10^0

Rev 2.1: Add test points
Rev 2.0: Initial design
File: PC218v2.kicad_sch Sheet: / Peter Farley

Id: 1/1 Title: Keithley 615 PC218 Replacement Board


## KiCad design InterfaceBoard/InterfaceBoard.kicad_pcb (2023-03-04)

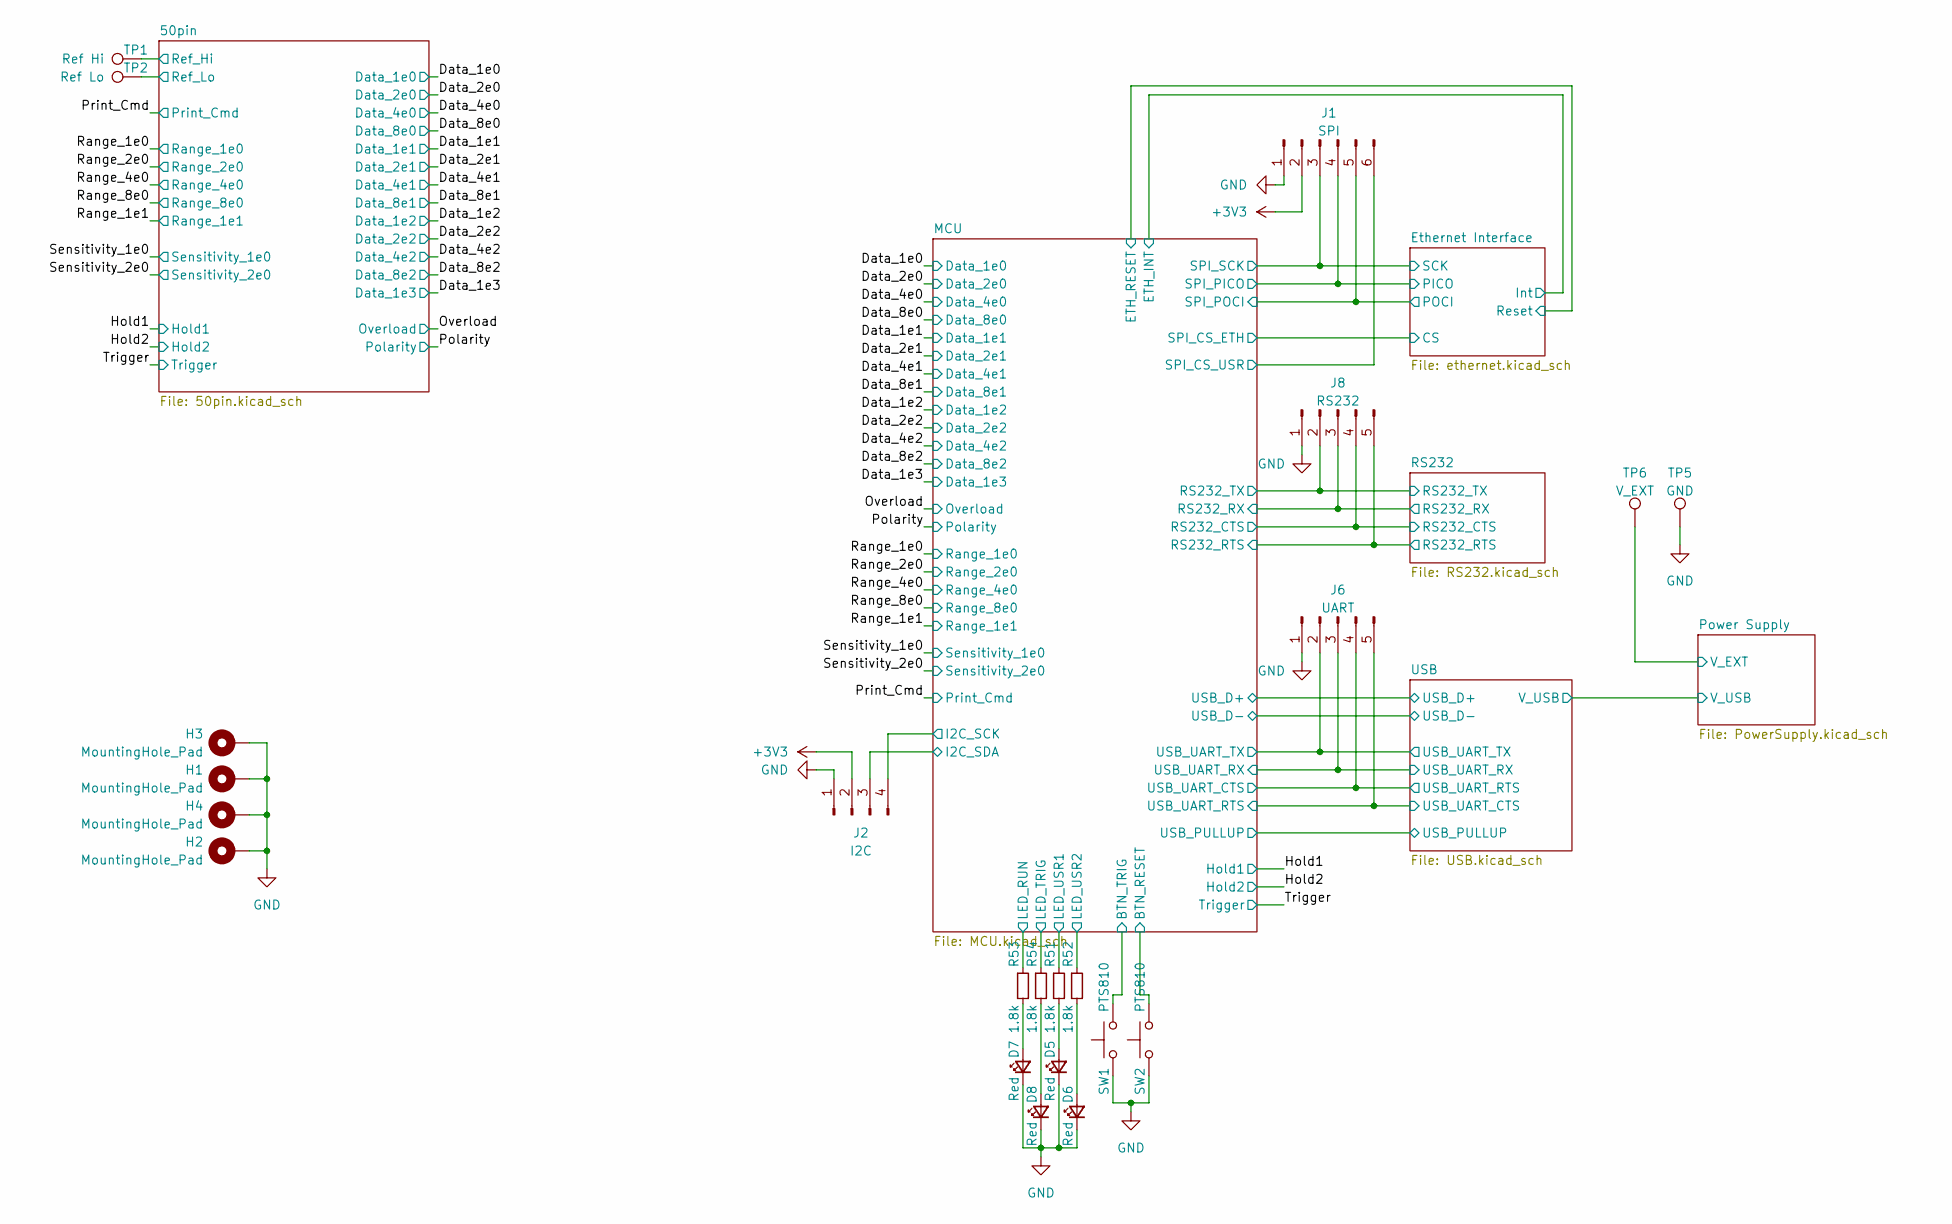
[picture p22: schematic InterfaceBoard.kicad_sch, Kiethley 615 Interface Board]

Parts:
D5, D6, D7, D8: Red; LED_0603_1608Metric
H1, H2, H3, H4: MountingHole_Pad; MountingHole_3.2mm_M3_Pad
J1: SPI; PinHeader_1x06_P1.27mm_Vertical
J2: I2C; PinHeader_1x04_P1.27mm_Vertical
J6: UART; PinHeader_1x05_P1.27mm_Vertical
J8: RS232; PinHeader_1x05_P1.27mm_Vertical
R51, R52, R53, R54: 1.8k; R_0603_1608Metric
SW1, SW2: PTS810; SW_SPST_PTS810
TP1: Ref Hi; TestPoint_Pad_1.5x1.5mm
TP2: Ref Lo; TestPoint_Pad_1.5x1.5mm
TP5: GND; TestPoint_THTPad_2.0x2.0mm_Drill1.0mm
TP6: V_EXT; TestPoint_THTPad_2.0x2.0mm_Drill1.0mm

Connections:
+3V3: J1.2, J2.2; also elsewhere on the board
/50pin/Ref_Hi: TP1.1; also elsewhere on the board
/50pin/Ref_Lo: TP2.1; also elsewhere on the board
/Ethernet Interface/PICO: J1.4; also elsewhere on the board
/Ethernet Interface/POCI: J1.5; also elsewhere on the board
/Ethernet Interface/SCK: J1.3; also elsewhere on the board
/MCU/BTN_TRIG: SW1.2; also elsewhere on the board
/MCU/I2C_SCK: J2.4; also elsewhere on the board
/MCU/I2C_SDA: J2.3; also elsewhere on the board
/MCU/LED_RUN: R53.1; also elsewhere on the board
/MCU/LED_TRIG: R54.1; also elsewhere on the board
/MCU/LED_USR1: R51.1; also elsewhere on the board
/MCU/LED_USR2: R52.1; also elsewhere on the board
/MCU/NRST: SW2.2; also elsewhere on the board
/MCU/RS232_CTS: J8.4; also elsewhere on the board
/MCU/RS232_RTS: J8.5; also elsewhere on the board
/MCU/RS232_RX: J8.3; also elsewhere on the board
/MCU/RS232_TX: J8.2; also elsewhere on the board
/MCU/SPI_CS_USR: J1.6; also elsewhere on the board
/MCU/USB_UART_CTS: J6.4; also elsewhere on the board
/MCU/USB_UART_RTS: J6.5; also elsewhere on the board
/MCU/USB_UART_RX: J6.3; also elsewhere on the board
/MCU/USB_UART_TX: J6.2; also elsewhere on the board
/Power Supply/V_EXT: TP6.1; also elsewhere on the board
GND: D5.1 (K), D6.1 (K), D7.1 (K), D8.1 (K), H1.1, H2.1, H3.1, H4.1, J1.1, J2.1, J6.1, J8.1, SW1.1, SW2.1, TP5.1; also elsewhere on the board
unnamed: D5.2 (A), R51.2
unnamed: D6.2 (A), R52.2
unnamed: D7.2 (A), R53.2
unnamed: D8.2 (A), R54.2

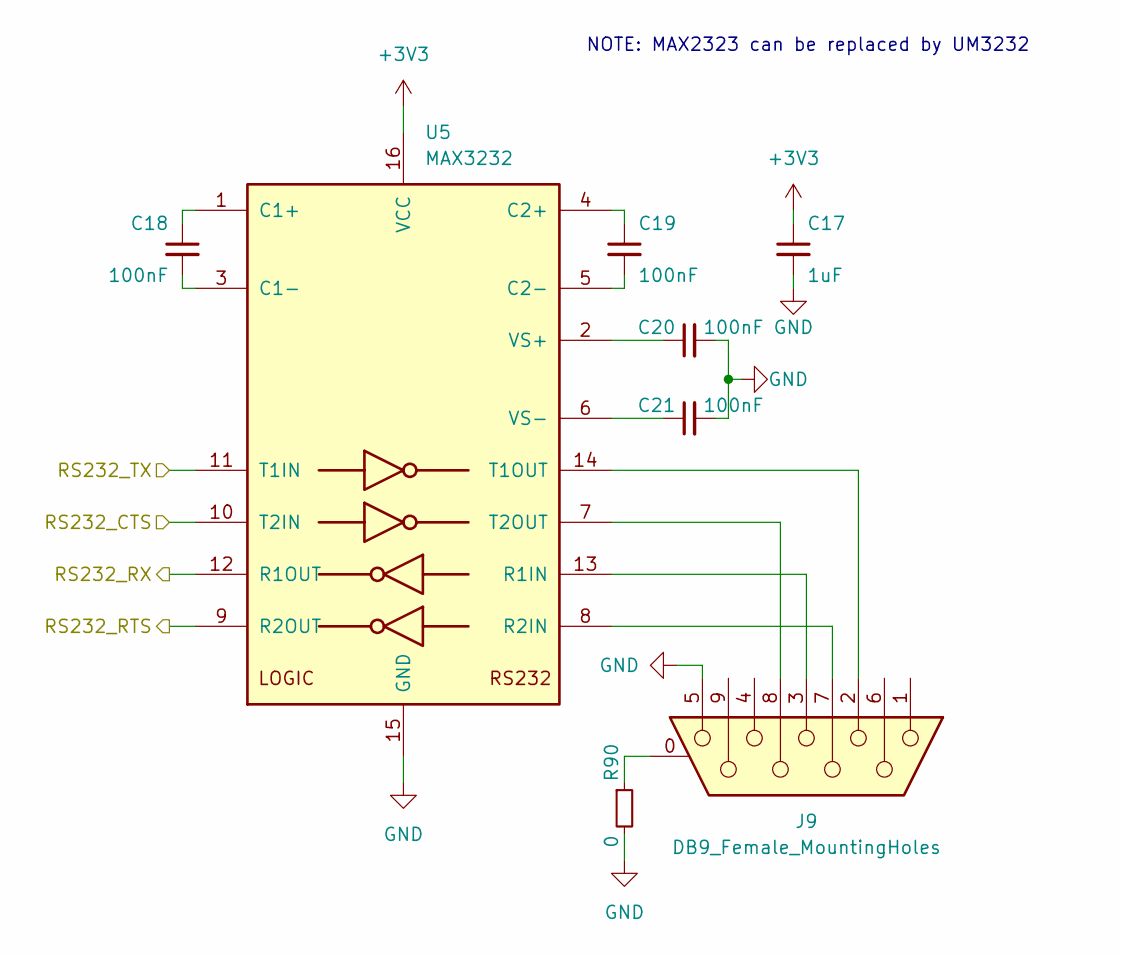
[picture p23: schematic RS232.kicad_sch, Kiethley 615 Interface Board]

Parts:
C17: 1uF; C_0603_1608Metric
C18, C19, C20, C21: 100nF; C_0603_1608Metric
J9: DB9_Female_MountingHoles; ASSMANN_A-DF_09_A_KG-T2S
R90: 0; R_0603_1608Metric
U5: MAX3232; SOIC-16_3.9x9.9mm_P1.27mm

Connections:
+3V3: C17.1, U5.16 (VCC); also elsewhere on the board
/MCU/RS232_CTS: U5.10 (T2IN); also elsewhere on the board
/MCU/RS232_RTS: U5.9 (R2OUT); also elsewhere on the board
/MCU/RS232_RX: U5.12 (R1OUT); also elsewhere on the board
/MCU/RS232_TX: U5.11 (T1IN); also elsewhere on the board
GND: C17.2, C20.2, C21.2, J9.5, R90.2, U5.15 (GND); also elsewhere on the board
unnamed: C18.1, U5.1 (C1+)
unnamed: C18.2, U5.3 (C1-)
unnamed: C19.1, U5.4 (C2+)
unnamed: C19.2, U5.5 (C2-)
unnamed: C20.1, U5.2 (VS+)
unnamed: C21.1, U5.6 (VS-)
unnamed: J9.0 (PAD), R90.1
unnamed: J9.2, U5.14 (T1OUT)
unnamed: J9.3, U5.13 (R1IN)
unnamed: J9.7, U5.8 (R2IN)
unnamed: J9.8, U5.7 (T2OUT)

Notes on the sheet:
NOTE: MAX2323 can be replaced by UM3232

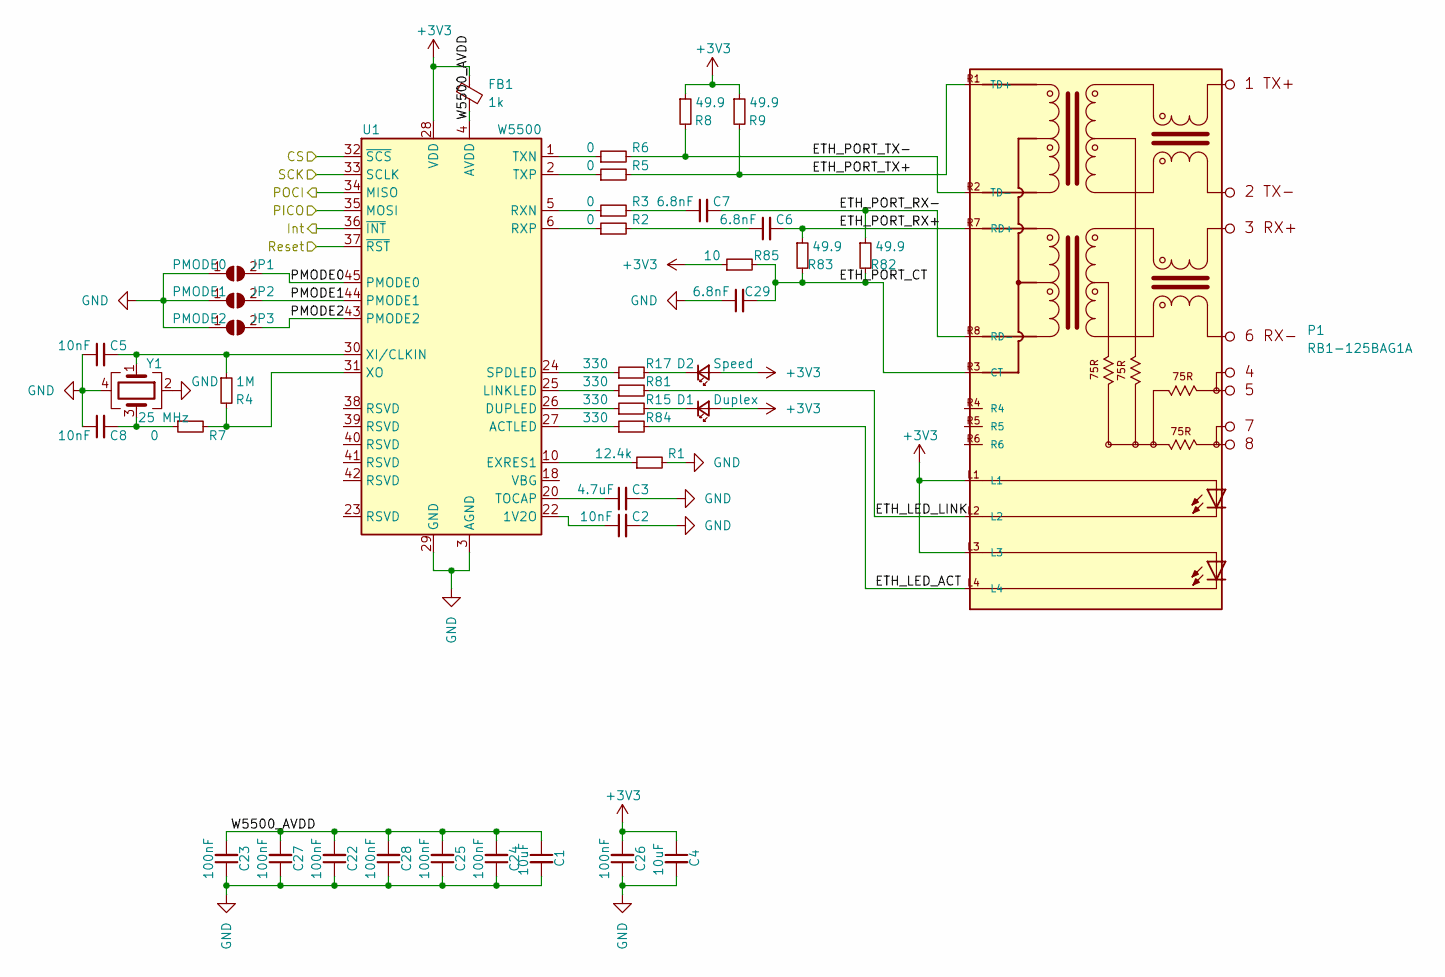
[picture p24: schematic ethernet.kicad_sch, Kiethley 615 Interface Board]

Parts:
C1, C4: 10uF; C_0805_2012Metric
C2, C5, C8: 10nF; C_0603_1608Metric
C3: 4.7uF; C_0603_1608Metric
C6, C7, C29: 6.8nF; C_0603_1608Metric
C22, C23, C24, C25, C26, C27, C28: 100nF; C_0603_1608Metric
D1: Duplex; LED_0603_1608Metric
D2: Speed; LED_0603_1608Metric
FB1: 1k; L_0805_2012Metric
JP1: PMODE0; 0603_solder_jumper
JP2: PMODE1; 0603_solder_jumper
JP3: PMODE2; 0603_solder_jumper
P1: RB1-125BAG1A; WIZNET_RB1-125BAG1A
R1: 12.4k; R_0603_1608Metric
R2, R3, R5, R6, R7: 0; R_0603_1608Metric
R4: 1M; R_0603_1608Metric
R8, R9, R82, R83: 49.9; R_0603_1608Metric
R15, R17, R81, R84: 330; R_0603_1608Metric
R85: 10; R_0603_1608Metric
U1: W5500; LQFP-48_7x7mm_P0.5mm
Y1: 25 MHz; Crystal_SMD_3225-4Pin_3.2x2.5mm

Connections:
+3V3: C4.1, C26.2, D1.2 (A), D2.2 (A), FB1.1, P1.L1, P1.L3, R8.1, R9.1, R85.1, U1.28 (VDD); also elsewhere on the board
/Ethernet Interface/CS: U1.32 (~SCS); also elsewhere on the board
/Ethernet Interface/ETH_LED_ACT: P1.L4, R84.2
/Ethernet Interface/ETH_LED_LINK: P1.L2, R81.2
/Ethernet Interface/ETH_PORT_CT: C29.2, P1.R3 (CT), R82.2, R83.2, R85.2
/Ethernet Interface/ETH_PORT_RX+: C6.2, P1.R7 (RD+), R83.1
/Ethernet Interface/ETH_PORT_RX-: C7.2, P1.R8 (RD-), R82.1
/Ethernet Interface/ETH_PORT_TX+: P1.R1 (TD+), R5.2, R9.2
/Ethernet Interface/ETH_PORT_TX-: P1.R2 (TD-), R6.2, R8.2
/Ethernet Interface/Int: U1.36 (~INT); also elsewhere on the board
/Ethernet Interface/PICO: U1.35 (MOSI); also elsewhere on the board
/Ethernet Interface/PMODE0: JP1.2 (B), U1.45 (PMODE0)
/Ethernet Interface/PMODE1: JP2.2 (B), U1.44 (PMODE1)
/Ethernet Interface/PMODE2: JP3.2 (B), U1.43 (PMODE2)
/Ethernet Interface/POCI: U1.34 (MISO); also elsewhere on the board
/Ethernet Interface/Reset: U1.37 (~RST); also elsewhere on the board
/Ethernet Interface/SCK: U1.33 (SCLK); also elsewhere on the board
/Ethernet Interface/W5500_AVDD: C1.1, C22.2, C23.2, C24.2, C25.2, C27.2, C28.2, FB1.2, U1.4 (AVDD), U1.8 (AVDD), U1.11 (AVDD), U1.15 (AVDD), U1.17 (AVDD), U1.21 (AVDD)
GND: C1.2, C2.2, C3.2, C4.2, C5.1, C8.1, C22.1, C23.1, C24.1, C25.1, C26.1, C27.1, C28.1, C29.1, JP1.1 (A), JP2.1 (A), JP3.1 (A), R1.2, U1.3 (AGND), U1.9 (AGND), U1.14 (AGND), U1.16 (AGND), U1.19 (AGND), U1.29 (GND), U1.48 (AGND), Y1.2, Y1.4; also elsewhere on the board
unnamed: C2.1, U1.22 (1V2O)
unnamed: C3.1, U1.20 (TOCAP)
unnamed: C5.2, R4.1, U1.30 (XI/CLKIN), Y1.1
unnamed: C6.1, R2.2
unnamed: C7.1, R3.2
unnamed: C8.2, R7.1, Y1.3
unnamed: D1.1 (K), R15.2
unnamed: D2.1 (K), R17.2
unnamed: R1.1, U1.10 (EXRES1)
unnamed: R2.1, U1.6 (RXP)
unnamed: R3.1, U1.5 (RXN)
unnamed: R4.2, R7.2, U1.31 (XO)
unnamed: R5.1, U1.2 (TXP)
unnamed: R6.1, U1.1 (TXN)
unnamed: R15.1, U1.26 (DUPLED)
unnamed: R17.1, U1.24 (SPDLED)
unnamed: R81.1, U1.25 (LINKLED)
unnamed: R84.1, U1.27 (ACTLED)

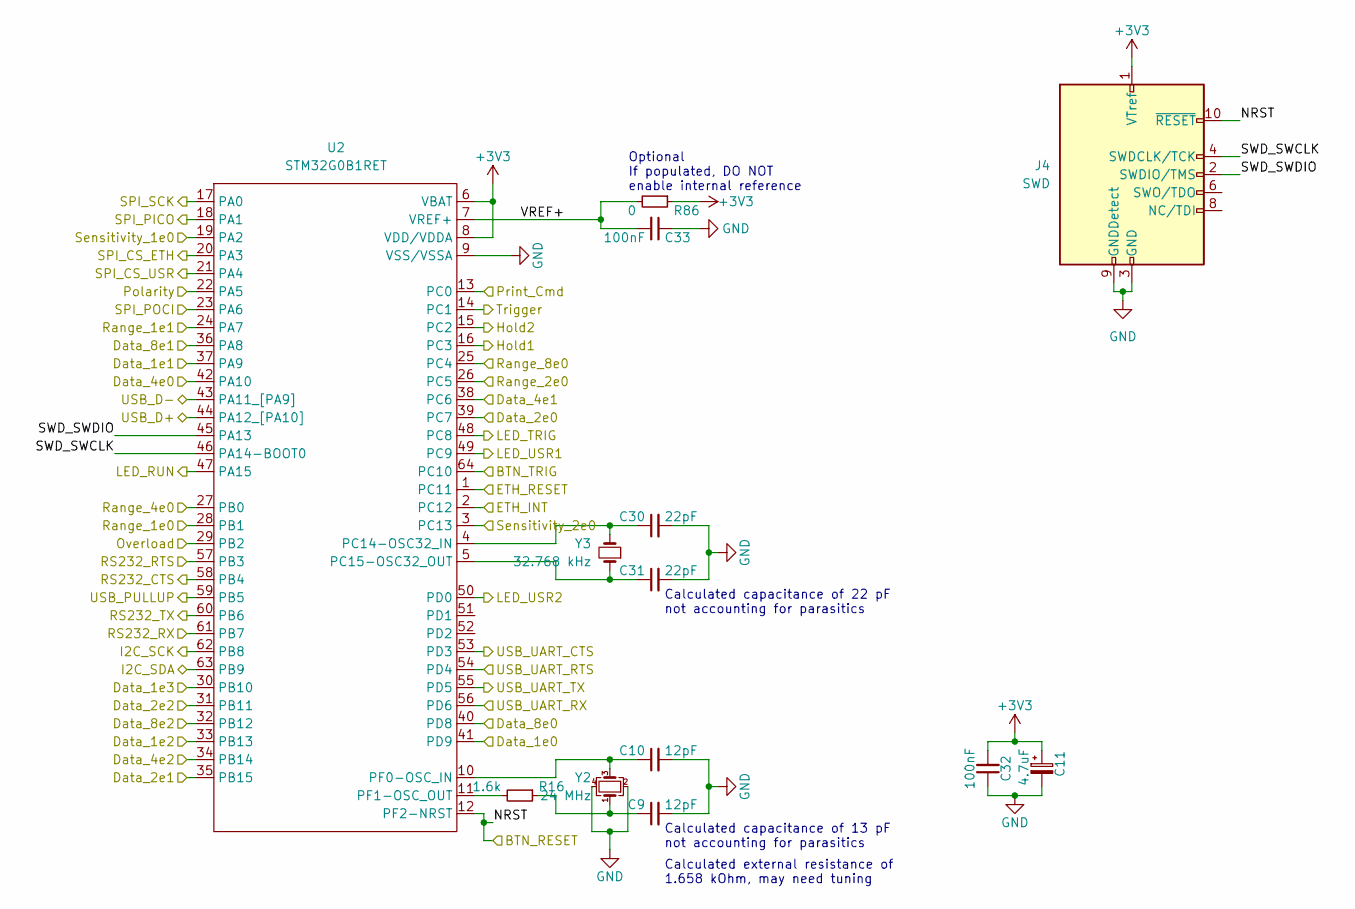
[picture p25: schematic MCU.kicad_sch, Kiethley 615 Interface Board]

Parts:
C9, C10: 12pF; C_0603_1608Metric
C11: 4.7uF; CP_Elec_5x5.9
C30, C31: 22pF; C_0603_1608Metric
C32, C33: 100nF; C_0603_1608Metric
J4: SWD; PinHeader_2x05_P1.27mm_Vertical
R16: 1.6k; R_0603_1608Metric
R86: 0; R_0603_1608Metric
U2: STM32G0B1RET; LQFP-64_10x10mm_P0.5mm
Y2: 24 MHz; Crystal_SMD_3225-4Pin_3.2x2.5mm
Y3: 32.768 kHz; Crystal_C26-LF_D2.1mm_L6.5mm_Horizontal

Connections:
+3V3: C11.1, C32.2, J4.1 (VTref), R86.1, U2.6 (VBAT), U2.8 (VDD/VDDA); also elsewhere on the board
/Data_1e0: U2.41 (PD9); also elsewhere on the board
/Data_1e1: U2.37 (PA9); also elsewhere on the board
/Data_1e2: U2.33 (PB13); also elsewhere on the board
/Data_1e3: U2.30 (PB10); also elsewhere on the board
/Data_2e0: U2.39 (PC7); also elsewhere on the board
/Data_2e1: U2.35 (PB15); also elsewhere on the board
/Data_2e2: U2.31 (PB11); also elsewhere on the board
/Data_4e0: U2.42 (PA10); also elsewhere on the board
/Data_4e1: U2.38 (PC6); also elsewhere on the board
/Data_4e2: U2.34 (PB14); also elsewhere on the board
/Data_8e0: U2.40 (PD8); also elsewhere on the board
/Data_8e1: U2.36 (PA8); also elsewhere on the board
/Data_8e2: U2.32 (PB12); also elsewhere on the board
/Ethernet Interface/CS: U2.20 (PA3); also elsewhere on the board
/Ethernet Interface/Int: U2.2 (PC12); also elsewhere on the board
/Ethernet Interface/PICO: U2.18 (PA1); also elsewhere on the board
/Ethernet Interface/POCI: U2.23 (PA6); also elsewhere on the board
/Ethernet Interface/Reset: U2.1 (PC11); also elsewhere on the board
/Ethernet Interface/SCK: U2.17 (PA0); also elsewhere on the board
/Hold1: U2.16 (PC3); also elsewhere on the board
/Hold2: U2.15 (PC2); also elsewhere on the board
/MCU/BTN_TRIG: U2.64 (PC10); also elsewhere on the board
/MCU/I2C_SCK: U2.62 (PB8); also elsewhere on the board
/MCU/I2C_SDA: U2.63 (PB9); also elsewhere on the board
/MCU/LED_RUN: U2.47 (PA15); also elsewhere on the board
/MCU/LED_TRIG: U2.48 (PC8); also elsewhere on the board
/MCU/LED_USR1: U2.49 (PC9); also elsewhere on the board
/MCU/LED_USR2: U2.50 (PD0); also elsewhere on the board
/MCU/NRST: J4.10 (~RESET), U2.12 (PF2-NRST); also elsewhere on the board
/MCU/RS232_CTS: U2.58 (PB4); also elsewhere on the board
/MCU/RS232_RTS: U2.57 (PB3); also elsewhere on the board
/MCU/RS232_RX: U2.61 (PB7); also elsewhere on the board
/MCU/RS232_TX: U2.60 (PB6); also elsewhere on the board
/MCU/SPI_CS_USR: U2.21 (PA4); also elsewhere on the board
/MCU/SWD_SWCLK: J4.4 (SWDCLK/TCK), U2.46 (PA14-BOOT0)
/MCU/SWD_SWDIO: J4.2 (SWDIO/TMS), U2.45 (PA13)
/MCU/USB_D+: U2.44 (PA12_[PA10]); also elsewhere on the board
/MCU/USB_D-: U2.43 (PA11_[PA9]); also elsewhere on the board
/MCU/USB_PULLUP: U2.59 (PB5); also elsewhere on the board
/MCU/USB_UART_CTS: U2.53 (PD3); also elsewhere on the board
/MCU/USB_UART_RTS: U2.54 (PD4); also elsewhere on the board
/MCU/USB_UART_RX: U2.56 (PD6); also elsewhere on the board
/MCU/USB_UART_TX: U2.55 (PD5); also elsewhere on the board
/MCU/VREF+: C33.2, R86.2, U2.7 (VREF+)
/Overload: U2.29 (PB2); also elsewhere on the board
/Polarity: U2.22 (PA5); also elsewhere on the board
/Print_Cmd: U2.13 (PC0); also elsewhere on the board
/Range_1e0: U2.28 (PB1); also elsewhere on the board
/Range_1e1: U2.24 (PA7); also elsewhere on the board
/Range_2e0: U2.26 (PC5); also elsewhere on the board
/Range_4e0: U2.27 (PB0); also elsewhere on the board
/Range_8e0: U2.25 (PC4); also elsewhere on the board
/Sensitivity_1e0: U2.19 (PA2); also elsewhere on the board
/Sensitivity_2e0: U2.3 (PC13); also elsewhere on the board
/Trigger: U2.14 (PC1); also elsewhere on the board
GND: C9.2, C10.2, C11.2, C30.2, C31.2, C32.1, C33.1, J4.3 (GND), J4.5 (GND), J4.9 (GNDDetect), U2.9 (VSS/VSSA), Y2.2, Y2.4; also elsewhere on the board
unnamed: C9.1, R16.1, Y2.1
unnamed: C10.1, U2.10 (PF0-OSC_IN), Y2.3
unnamed: C30.1, U2.4 (PC14-OSC32_IN), Y3.2
unnamed: C31.1, U2.5 (PC15-OSC32_OUT), Y3.1
unnamed: R16.2, U2.11 (PF1-OSC_OUT)

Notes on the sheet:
Calculated external resistance of 1.658 kOhm, may need tuning
Calculated capacitance of 13 pF not accounting for parasitics
Calculated capacitance of 22 pF not accounting for parasitics
Optional If populated, DO NOT enable internal reference

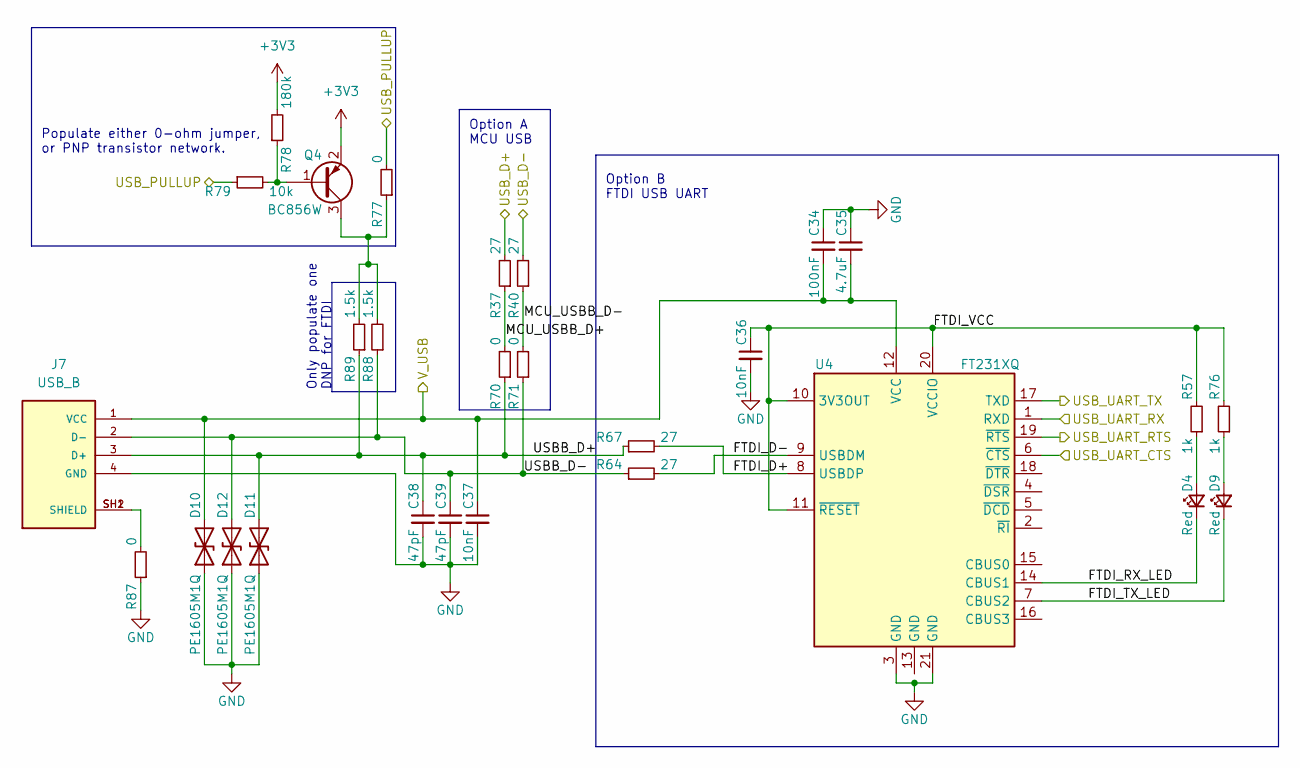
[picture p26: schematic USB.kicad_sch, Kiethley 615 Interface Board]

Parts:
C34: 100nF; C_0603_1608Metric
C35: 4.7uF; C_0603_1608Metric
C36, C37: 10nF; C_0603_1608Metric
C38, C39: 47pF; C_0603_1608Metric
D4, D9: Red; LED_0603_1608Metric
D10, D11, D12: PE1605M1Q; D_0402_1005Metric
J7: USB_B; CUI_UJ2-BH-W1-TH; PART_REV 1.0
Q4: BC856W; SOT-323_SC-70
R37, R40, R64, R67: 27; R_0603_1608Metric
R57, R76: 1k; R_0603_1608Metric
R70, R71, R77, R87: 0; R_0603_1608Metric
R78: 180k; R_0603_1608Metric
R79: 10k; R_0603_1608Metric
R88, R89: 1.5k; R_0603_1608Metric
U4: FT231XQ; QFN-20-1EP_4x4mm_P0.5mm_EP2.5x2.5mm

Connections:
+3V3: Q4.2 (E), R78.2; also elsewhere on the board
/MCU/USB_D+: R37.2; also elsewhere on the board
/MCU/USB_D-: R40.2; also elsewhere on the board
/MCU/USB_PULLUP: R77.2, R79.1; also elsewhere on the board
/MCU/USB_UART_CTS: U4.19 (~RTS); also elsewhere on the board
/MCU/USB_UART_RTS: U4.6 (~CTS); also elsewhere on the board
/MCU/USB_UART_RX: U4.1 (RXD); also elsewhere on the board
/MCU/USB_UART_TX: U4.17 (TXD); also elsewhere on the board
/Power Supply/V_USB: C34.2, C35.2, C37.1, D10.2 (A2), J7.1 (VCC), U4.12 (VCC); also elsewhere on the board
/USB/FTDI_D+: R67.2, U4.8 (USBDP)
/USB/FTDI_D-: R64.2, U4.9 (USBDM)
/USB/FTDI_RX_LED: D4.1 (K), U4.14 (CBUS1)
/USB/FTDI_TX_LED: D9.1 (K), U4.7 (CBUS2)
/USB/FTDI_VCC: C36.1, R57.2, R76.2, U4.10 (3V3OUT), U4.11 (~RESET), U4.20 (VCCIO)
/USB/MCU_USBB_D+: R37.1, R70.2
/USB/MCU_USBB_D-: R40.1, R71.2
/USB/USBB_D+: C38.1, D11.2 (A2), J7.3 (D+), R67.1, R70.1, R89.1
/USB/USBB_D-: C39.1, D12.2 (A2), J7.2 (D-), R64.1, R71.1, R88.1
GND: C34.1, C35.1, C36.2, C37.2, C38.2, C39.2, D10.1 (A1), D11.1 (A1), D12.1 (A1), J7.4 (GND), R87.1, U4.3 (GND), U4.21 (GND); also elsewhere on the board
unnamed: D4.2 (A), R57.1
unnamed: D9.2 (A), R76.1
unnamed: J7.SH1 (SHIELD), J7.SH2 (SHIELD), R87.2
unnamed: Q4.1 (B), R78.1, R79.2
unnamed: Q4.3 (C), R77.1, R88.2, R89.2

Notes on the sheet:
Option A MCU USB
Populate either 0-ohm jumper, or PNP transistor network.
Option B FTDI USB UART
Only populate one DNP for FTDI

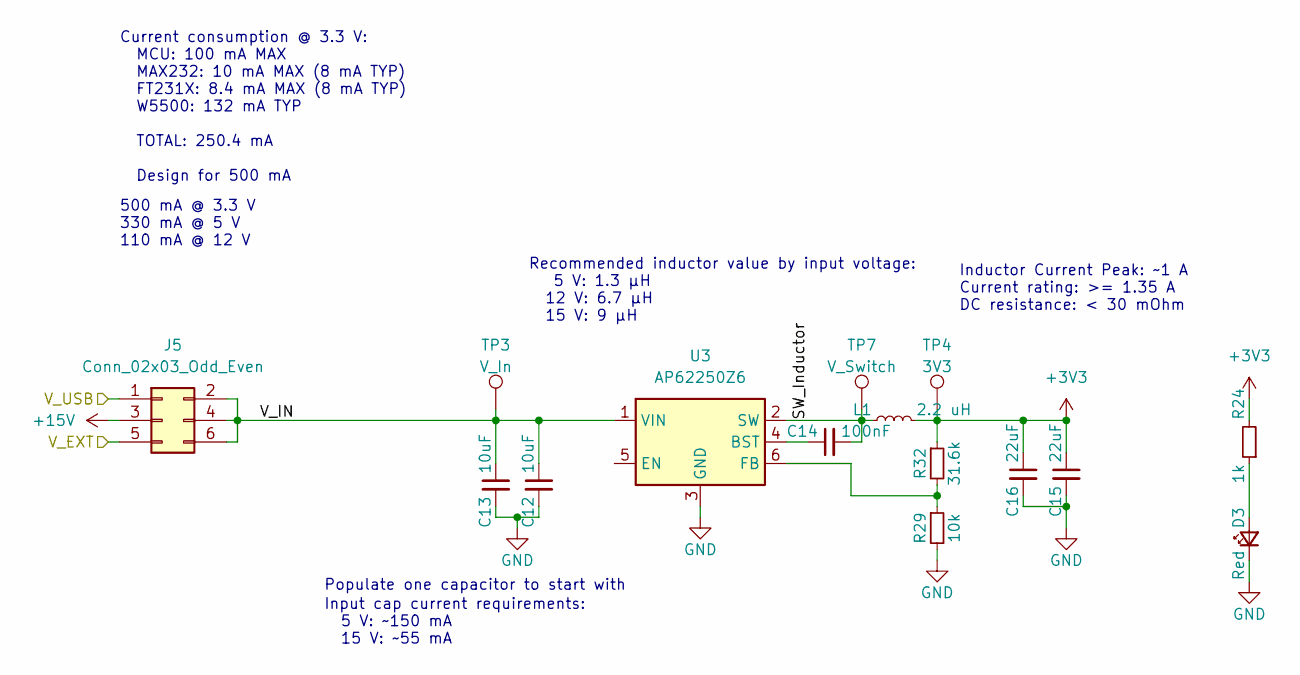
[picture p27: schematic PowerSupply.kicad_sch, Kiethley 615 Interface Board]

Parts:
C12, C13: 10uF; C_0805_2012Metric
C14: 100nF; C_0603_1608Metric
C15, C16: 22uF; C_0805_2012Metric
D3: Red; LED_0603_1608Metric
J5: Conn_02x03_Odd_Even; PinHeader_2x03_P1.27mm_Vertical
L1: 2.2 uH; L_Taiyo-Yuden_NR-50xx
R24: 1k; R_0603_1608Metric
R29: 10k; R_0603_1608Metric
R32: 31.6k; R_0603_1608Metric
TP3: V_In; TestPoint_THTPad_1.5x1.5mm_Drill0.7mm
TP4: 3V3; TestPoint_THTPad_1.5x1.5mm_Drill0.7mm
TP7: V_Switch; TestPoint_THTPad_1.5x1.5mm_Drill0.7mm
U3: AP62250Z6; SOT-563

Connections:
+3V3: C15.1, C16.1, L1.2, R24.2, R32.1, TP4.1; also elsewhere on the board
+15V: J5.3; also elsewhere on the board
/Power Supply/SW_Inductor: C14.2, L1.1, TP7.1, U3.2 (SW)
/Power Supply/V_EXT: J5.5; also elsewhere on the board
/Power Supply/V_IN: C12.1, C13.1, J5.2, J5.4, J5.6, TP3.1, U3.1 (VIN)
/Power Supply/V_USB: J5.1; also elsewhere on the board
GND: C12.2, C13.2, C15.2, C16.2, D3.1 (K), R29.2, U3.3 (GND); also elsewhere on the board
unnamed: C14.1, U3.4 (BST)
unnamed: D3.2 (A), R24.1
unnamed: R29.1, R32.2, U3.6 (FB)

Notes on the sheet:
Input cap current requirements: 5 V: ~150 mA 15 V: ~55 mA
Current consumption @ 3.3 V: MCU: 100 mA MAX MAX232: 10 mA MAX (8 mA TYP) FT231X: 8.4 mA MAX (8 mA TYP) W5500: 132 mA TYP TOTAL: 250.4 mA Design for 500 mA
Inductor Current Peak: ~1 A Current rating: >= 1.35 A DC resistance: < 30 mOhm
500 mA @ 3.3 V 330 mA @ 5 V 110 mA @ 12 V
Recommended inductor value by input voltage: 5 V: 1.3 µH 12 V: 6.7 µH 15 V: 9 µH
Populate one capacitor to start with

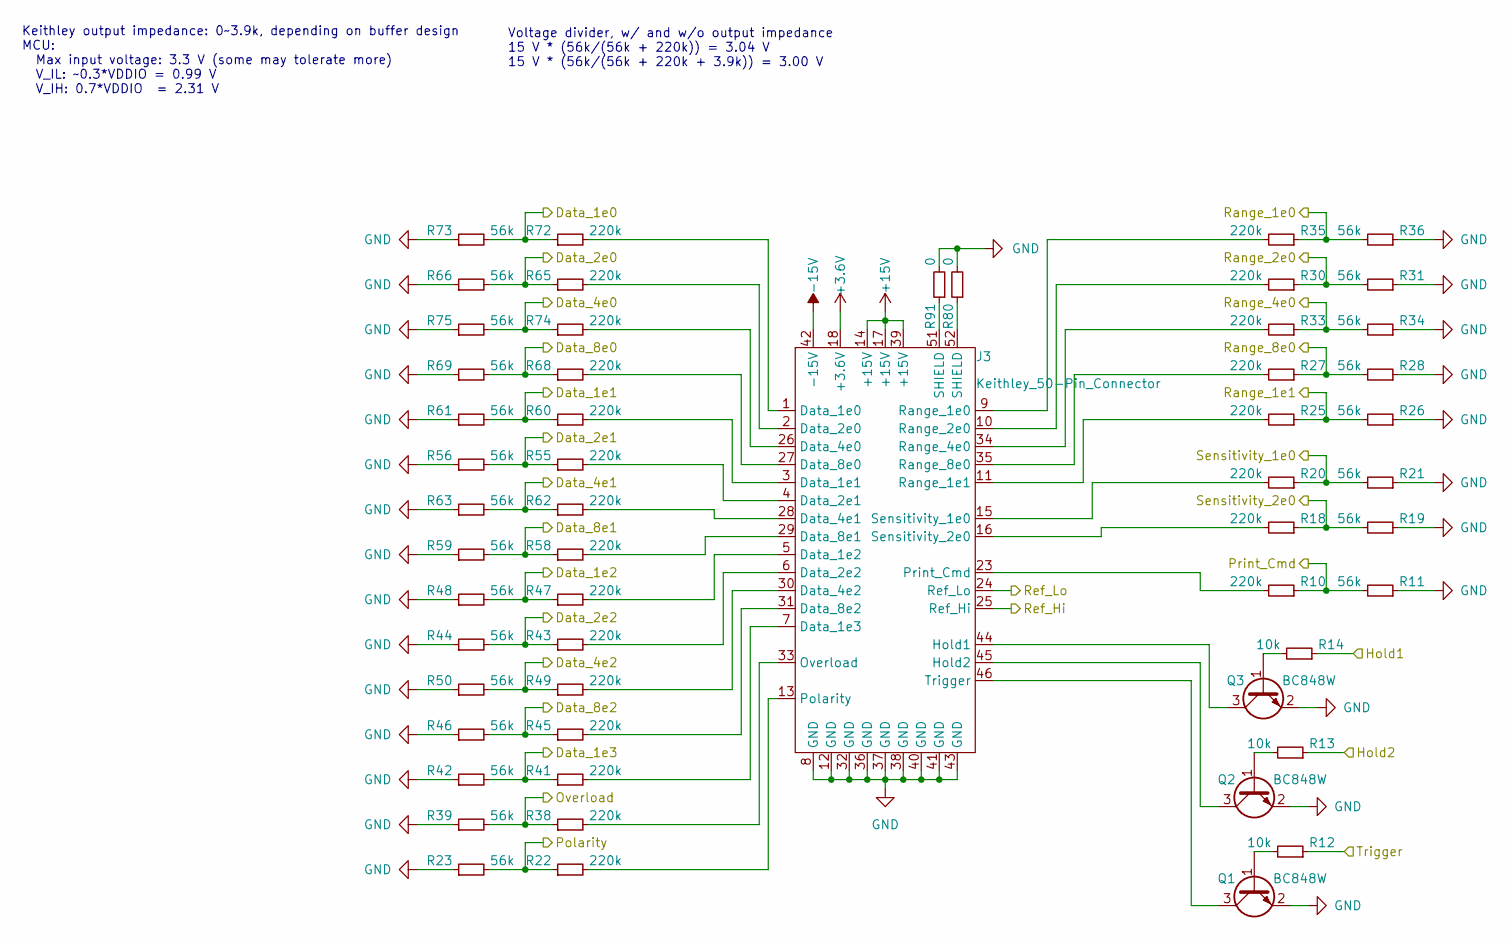
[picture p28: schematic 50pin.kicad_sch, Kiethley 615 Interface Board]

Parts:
J3: Keithley_50-Pin_Connector; NorComp_112-050-213R001
Q1, Q2, Q3: BC848W; SOT-323_SC-70
R10, R18, R20, R22, R25, R27, R30, R33, R35, R38, R41, R43, R45, R47, R49, R55, R58, R60, R62, R65, R68, R72, R74: 220k; R_0603_1608Metric
R11, R19, R21, R23, R26, R28, R31, R34, R36, R39, R42, R44, R46, R48, R50, R56, R59, R61, R63, R66, R69, R73, R75: 56k; R_0603_1608Metric
R12, R13, R14: 10k; R_0603_1608Metric
R80, R91: 0; R_0603_1608Metric

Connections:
+3.6V: J3.18 (+3.6V)
+15V: J3.14 (+15V), J3.17 (+15V), J3.39 (+15V); also elsewhere on the board
-15V: J3.42 (-15V)
/50pin/Ref_Hi: J3.25 (Ref_Hi); also elsewhere on the board
/50pin/Ref_Lo: J3.24 (Ref_Lo); also elsewhere on the board
/Data_1e0: R72.1, R73.2; also elsewhere on the board
/Data_1e1: R60.1, R61.2; also elsewhere on the board
/Data_1e2: R47.1, R48.2; also elsewhere on the board
/Data_1e3: R41.1, R42.2; also elsewhere on the board
/Data_2e0: R65.1, R66.2; also elsewhere on the board
/Data_2e1: R55.1, R56.2; also elsewhere on the board
/Data_2e2: R43.1, R44.2; also elsewhere on the board
/Data_4e0: R74.1, R75.2; also elsewhere on the board
/Data_4e1: R62.1, R63.2; also elsewhere on the board
/Data_4e2: R49.1, R50.2; also elsewhere on the board
/Data_8e0: R68.1, R69.2; also elsewhere on the board
/Data_8e1: R58.1, R59.2; also elsewhere on the board
/Data_8e2: R45.1, R46.2; also elsewhere on the board
/Hold1: R14.1; also elsewhere on the board
/Hold2: R13.1; also elsewhere on the board
/Overload: R38.1, R39.2; also elsewhere on the board
/Polarity: R22.1, R23.2; also elsewhere on the board
/Print_Cmd: R10.1, R11.2; also elsewhere on the board
/Range_1e0: R35.1, R36.2; also elsewhere on the board
/Range_1e1: R25.1, R26.2; also elsewhere on the board
/Range_2e0: R30.1, R31.2; also elsewhere on the board
/Range_4e0: R33.1, R34.2; also elsewhere on the board
/Range_8e0: R27.1, R28.2; also elsewhere on the board
/Sensitivity_1e0: R20.1, R21.2; also elsewhere on the board
/Sensitivity_2e0: R18.1, R19.2; also elsewhere on the board
/Trigger: R12.1; also elsewhere on the board
GND: J3.8 (GND), J3.12 (GND), J3.32 (GND), J3.36 (GND), J3.37 (GND), J3.38 (GND), J3.40 (GND), J3.41 (GND), J3.43 (GND), Q1.2 (E), Q2.2 (E), Q3.2 (E), R11.1, R19.1, R21.1, R23.1, R26.1, R28.1, R31.1, R34.1, R36.1, R39.1, R42.1, R44.1, R46.1, R48.1, R50.1, R56.1, R59.1, R61.1, R63.1, R66.1, R69.1, R73.1, R75.1, R80.2, R91.2; also elsewhere on the board
unnamed: J3.1 (Data_1e0), R72.2
unnamed: J3.2 (Data_2e0), R65.2
unnamed: J3.3 (Data_1e1), R60.2
unnamed: J3.4 (Data_2e1), R55.2
unnamed: J3.5 (Data_1e2), R47.2
unnamed: J3.6 (Data_2e2), R43.2
unnamed: J3.7 (Data_1e3), R41.2
unnamed: J3.9 (Range_1e0), R35.2
unnamed: J3.10 (Range_2e0), R30.2
unnamed: J3.11 (Range_1e1), R25.2
unnamed: J3.13 (Polarity), R22.2
unnamed: J3.15 (Sensitivity_1e0), R20.2
unnamed: J3.16 (Sensitivity_2e0), R18.2
unnamed: J3.23 (Print_Cmd), R10.2
unnamed: J3.26 (Data_4e0), R74.2
unnamed: J3.27 (Data_8e0), R68.2
unnamed: J3.28 (Data_4e1), R62.2
unnamed: J3.29 (Data_8e1), R58.2
unnamed: J3.30 (Data_4e2), R49.2
unnamed: J3.31 (Data_8e2), R45.2
unnamed: J3.33 (Overload), R38.2
unnamed: J3.34 (Range_4e0), R33.2
unnamed: J3.35 (Range_8e0), R27.2
unnamed: J3.44 (Hold1), Q3.3 (C)
unnamed: J3.45 (Hold2), Q2.3 (C)
unnamed: J3.46 (Trigger), Q1.3 (C)
unnamed: J3.51 (SHIELD), R91.1
unnamed: J3.52 (SHIELD), R80.1
unnamed: Q1.1 (B), R12.2
unnamed: Q2.1 (B), R13.2
unnamed: Q3.1 (B), R14.2

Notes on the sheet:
Voltage divider, w/ and w/o output impedance 15 V * (56k/(56k + 220k)) = 3.04 V 15 V * (56k/(56k + 220k + 3.9k)) = 3.00 V
Keithley output impedance: 0~3.9k, depending on buffer design MCU: Max input voltage: 3.3 V (some may tolerate more) V_IL: ~0.3*VDDIO = 0.99 V V_IH: 0.7*VDDIO = 2.31 V

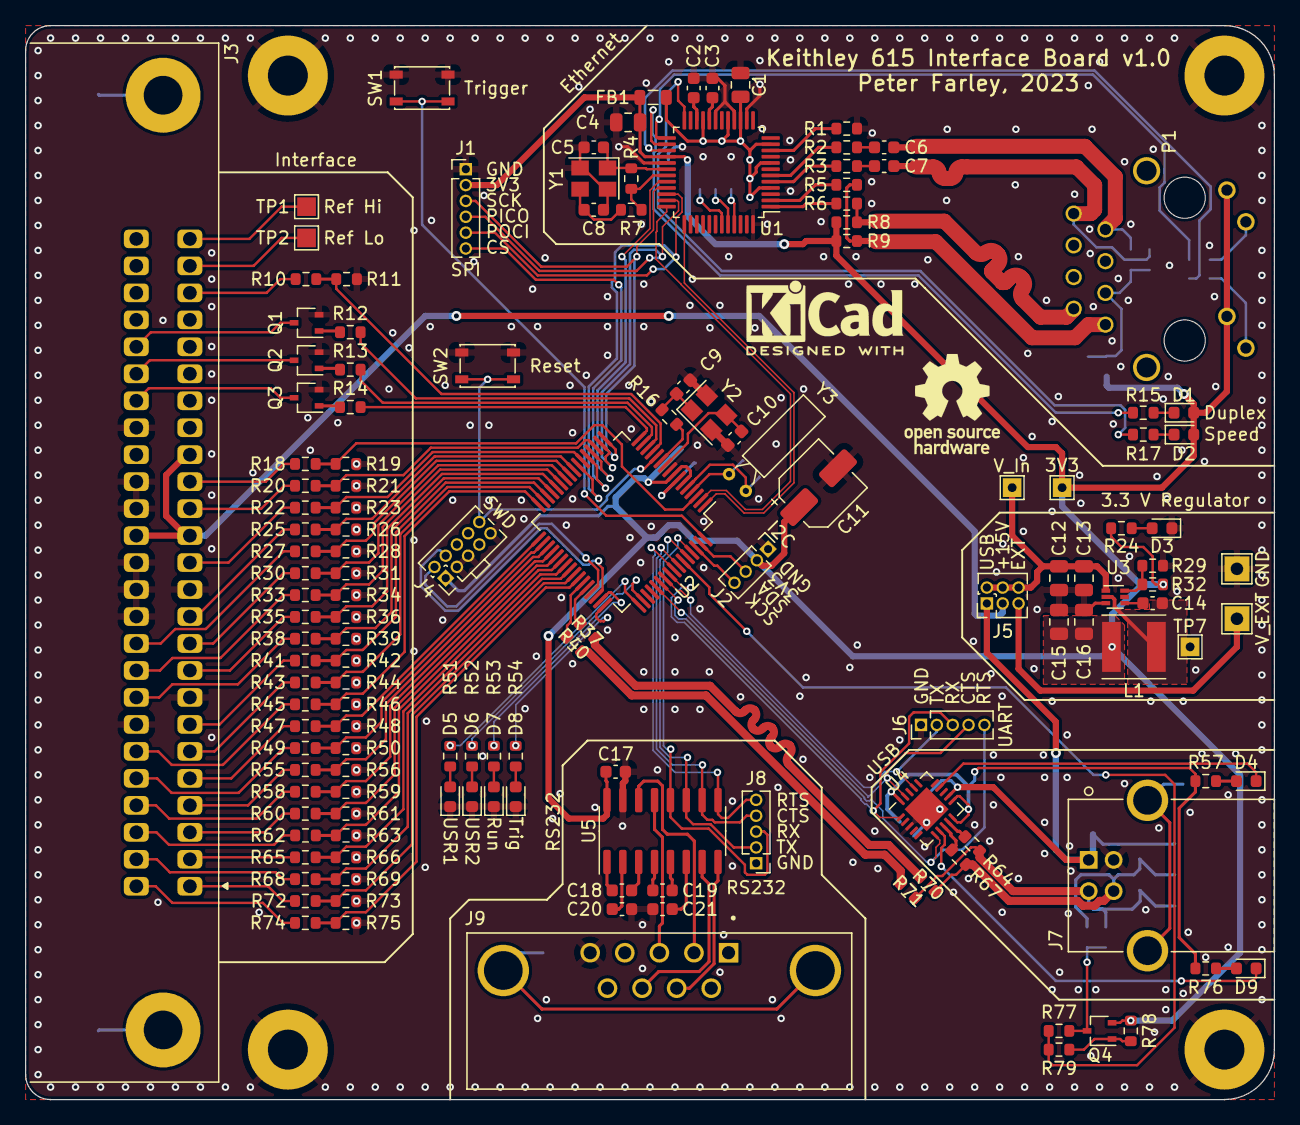
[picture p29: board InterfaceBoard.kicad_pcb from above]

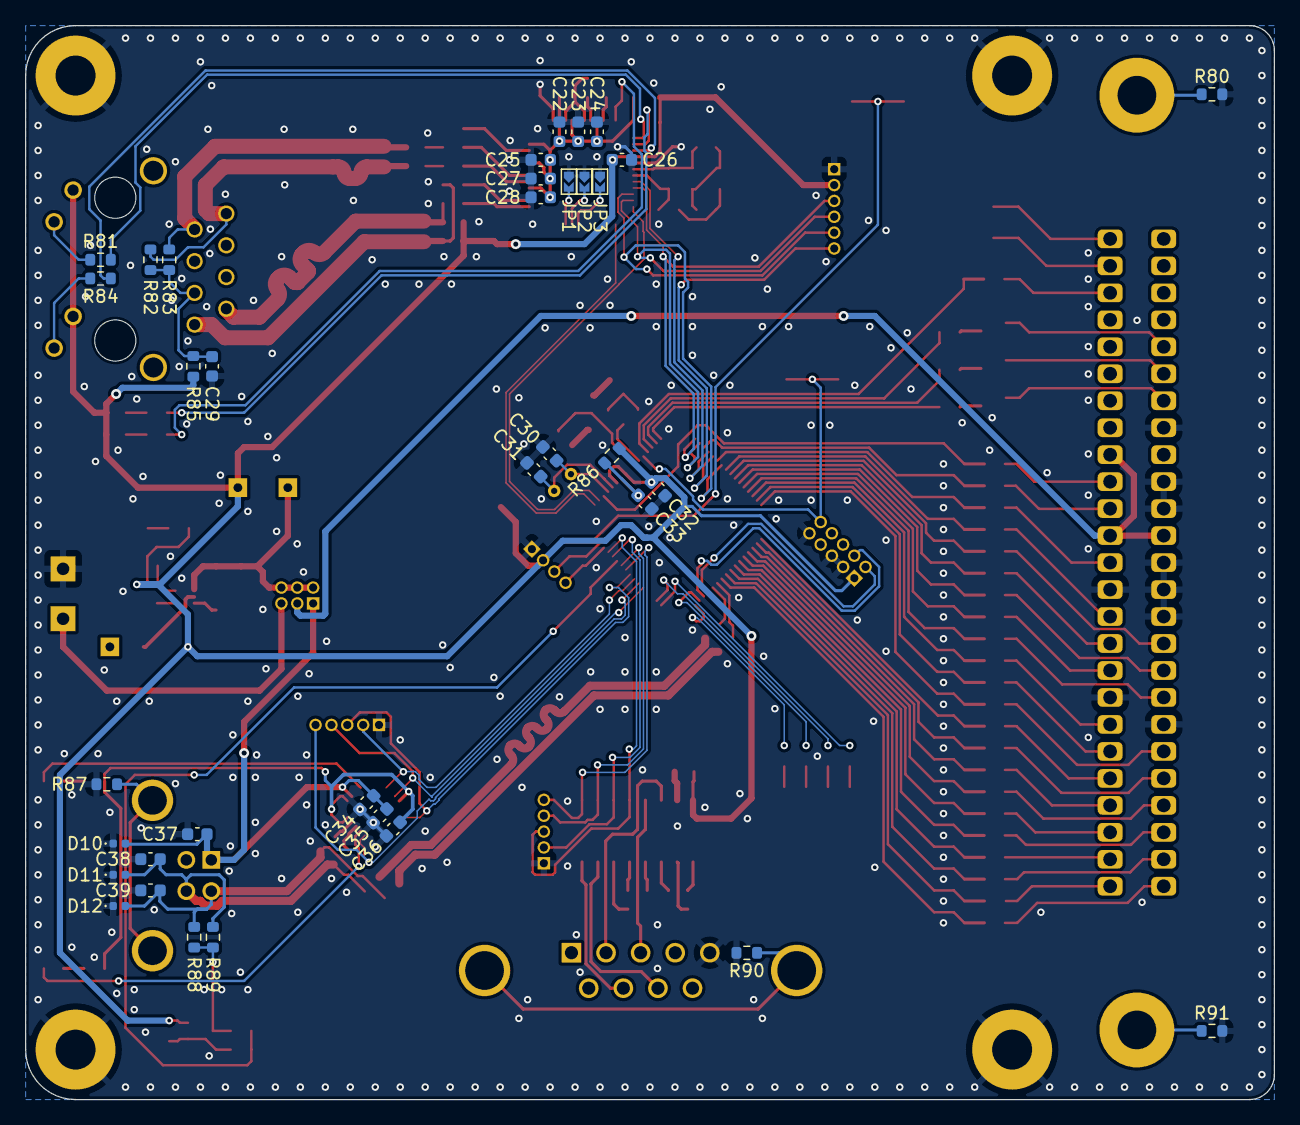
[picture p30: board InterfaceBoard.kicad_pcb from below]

Board: 2 copper layers, 100.0 x 86.0 mm, 182 parts (36 on the bottom side), 161 nets.

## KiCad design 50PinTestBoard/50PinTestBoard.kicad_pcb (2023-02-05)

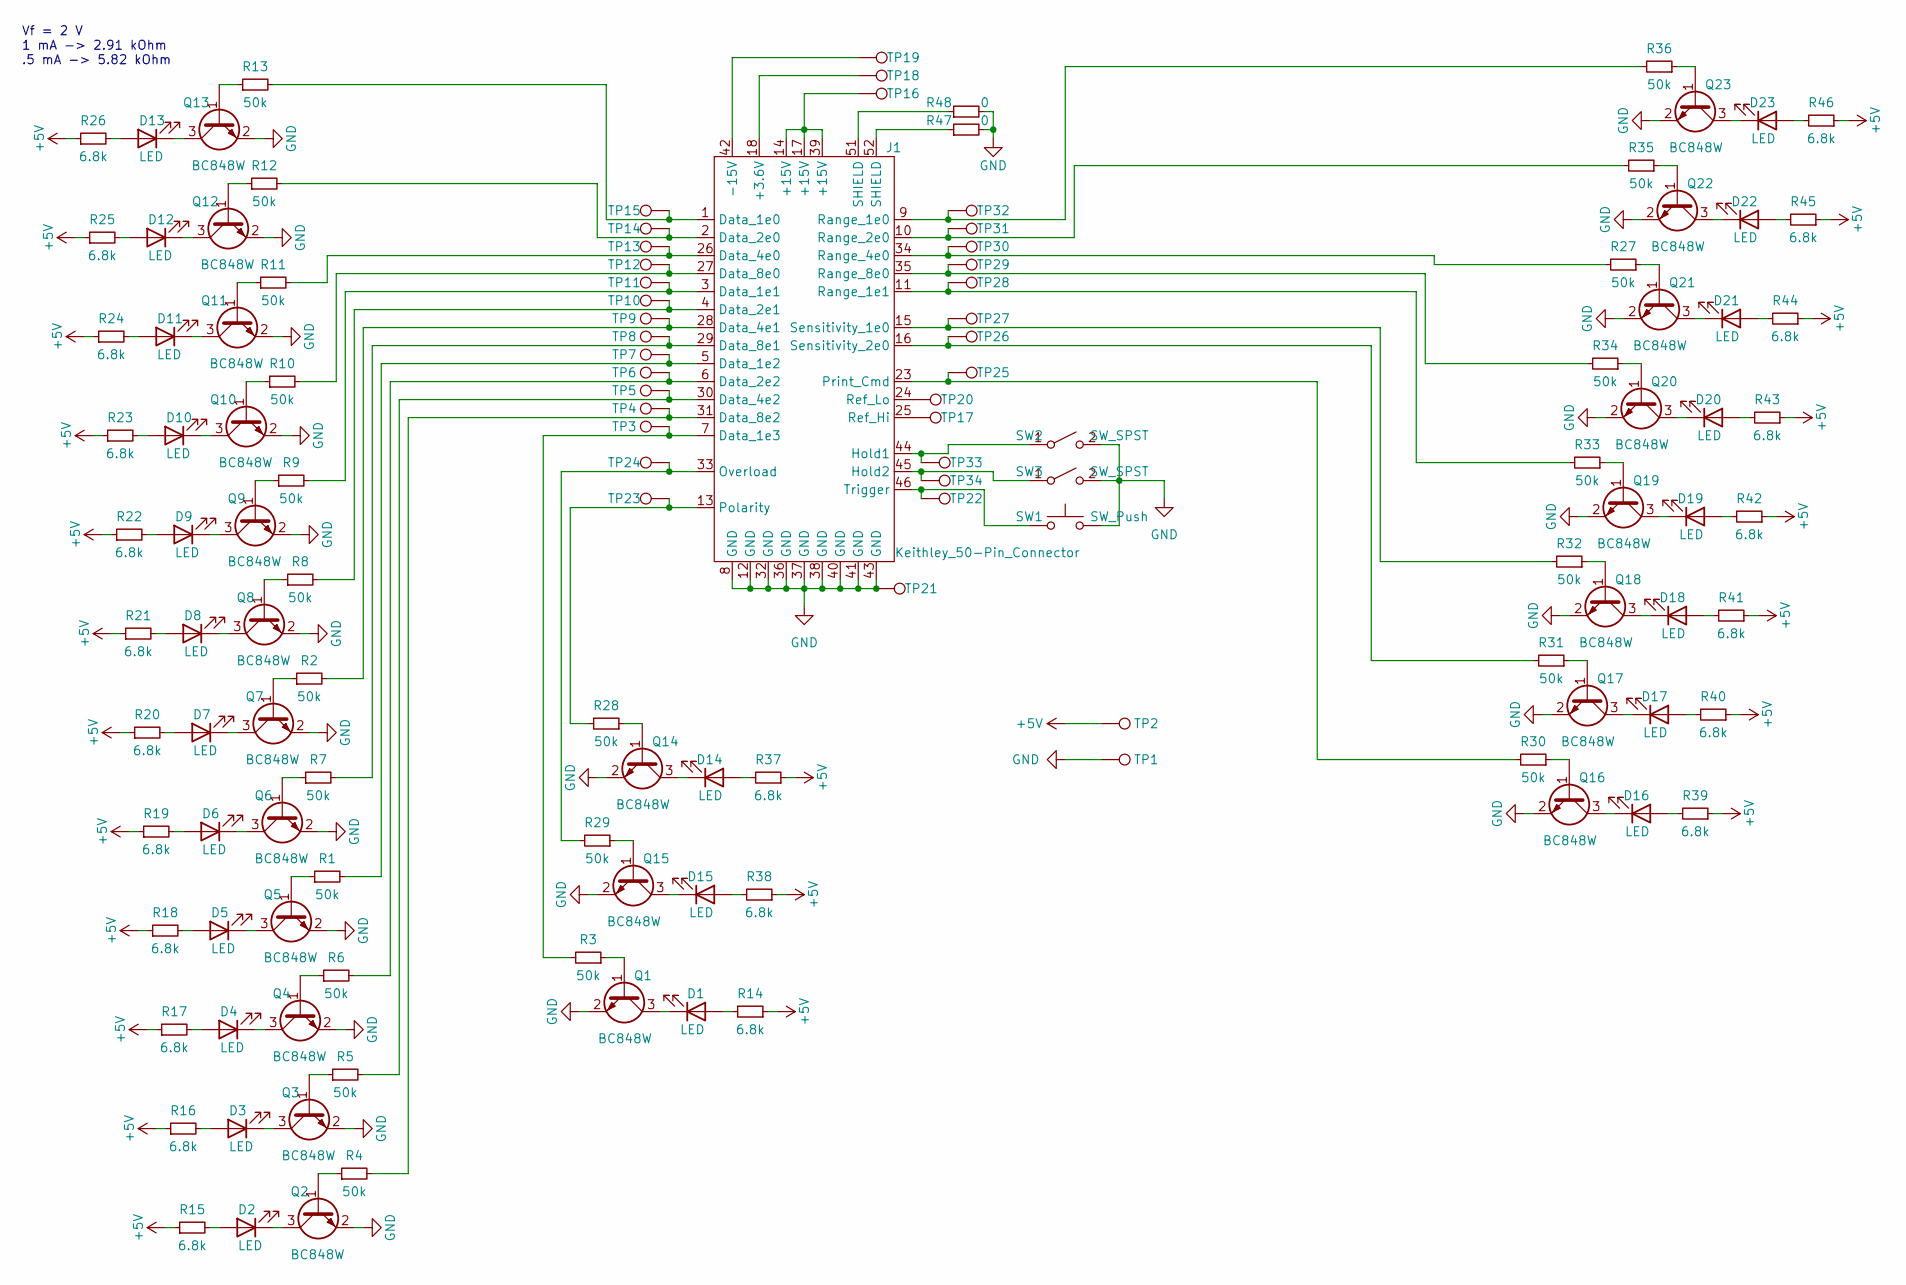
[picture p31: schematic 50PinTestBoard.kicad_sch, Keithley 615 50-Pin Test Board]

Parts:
D1, D2, D3, D4, D5, D6, D7, D8, D9, D10, D11, D12, D13, D14, D15, D16, D17, D18, D19, D20, D21, D22, D23: LED; LED_0603_1608Metric
J1: Keithley_50-Pin_Connector; NorComp_112-050-213R001
Q1, Q2, Q3, Q4, Q5, Q6, Q7, Q8, Q9, Q10, Q11, Q12, Q13, Q14, Q15, Q16, Q17, Q18, Q19, Q20, Q21, Q22, Q23: BC848W; SOT-323_SC-70
R1, R2, R3, R4, R5, R6, R7, R8, R9, R10, R11, R12, R13, R27, R28, R29, R30, R31, R32, R33, R34, R35, R36: 50k; R_0603_1608Metric
R14, R15, R16, R17, R18, R19, R20, R21, R22, R23, R24, R25, R26, R37, R38, R39, R40, R41, R42, R43, R44, R45, R46: 6.8k; R_0603_1608Metric
R47, R48: 0; R_0603_1608Metric
SW1: SW_Push; SW_SPST_PTS810
SW2, SW3: SW_SPST; SW_SPDT_CK-JS102011SAQN
TP1, TP2, TP3, TP4, TP5, TP6, TP7, TP8, TP9, TP10, TP11, TP12, TP13, TP14, TP15, TP16, TP17, TP18, TP19, TP20, TP21, TP22, TP23, TP24, TP25, TP26, TP27, TP28, TP29, TP30, TP31, TP32, TP33, TP34: TestPoint; TestPoint_THTPad_2.0x2.0mm_Drill1.0mm

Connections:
+5V: R14.1, R15.1, R16.1, R17.1, R18.1, R19.1, R20.1, R21.1, R22.1, R23.1, R24.1, R25.1, R26.1, R37.1, R38.1, R39.1, R40.1, R41.1, R42.1, R43.1, R44.1, R45.1, R46.1, TP2.1
GND: J1.8 (GND), J1.12 (GND), J1.32 (GND), J1.36 (GND), J1.37 (GND), J1.38 (GND), J1.40 (GND), J1.41 (GND), J1.43 (GND), Q1.2 (E), Q2.2 (E), Q3.2 (E), Q4.2 (E), Q5.2 (E), Q6.2 (E), Q7.2 (E), Q8.2 (E), Q9.2 (E), Q10.2 (E), Q11.2 (E), Q12.2 (E), Q13.2 (E), Q14.2 (E), Q15.2 (E), Q16.2 (E), Q17.2 (E), Q18.2 (E), Q19.2 (E), Q20.2 (E), Q21.2 (E), Q22.2 (E), Q23.2 (E), R47.2, R48.2, SW1.2, SW2.2 (B), SW3.2 (B), TP1.1, TP21.1
unnamed: D1.1 (K), Q1.3 (C)
unnamed: D1.2 (A), R14.2
unnamed: D2.1 (K), Q2.3 (C)
unnamed: D2.2 (A), R15.2
unnamed: D3.1 (K), Q3.3 (C)
unnamed: D3.2 (A), R16.2
unnamed: D4.1 (K), Q4.3 (C)
unnamed: D4.2 (A), R17.2
unnamed: D5.1 (K), Q5.3 (C)
unnamed: D5.2 (A), R18.2
unnamed: D6.1 (K), Q6.3 (C)
unnamed: D6.2 (A), R19.2
unnamed: D7.1 (K), Q7.3 (C)
unnamed: D7.2 (A), R20.2
unnamed: D8.1 (K), Q8.3 (C)
unnamed: D8.2 (A), R21.2
unnamed: D9.1 (K), Q9.3 (C)
unnamed: D9.2 (A), R22.2
unnamed: D10.1 (K), Q10.3 (C)
unnamed: D10.2 (A), R23.2
unnamed: D11.1 (K), Q11.3 (C)
unnamed: D11.2 (A), R24.2
unnamed: D12.1 (K), Q12.3 (C)
unnamed: D12.2 (A), R25.2
unnamed: D13.1 (K), Q13.3 (C)
unnamed: D13.2 (A), R26.2
unnamed: D14.1 (K), Q14.3 (C)
unnamed: D14.2 (A), R37.2
unnamed: D15.1 (K), Q15.3 (C)
unnamed: D15.2 (A), R38.2
unnamed: D16.1 (K), Q16.3 (C)
unnamed: D16.2 (A), R39.2
unnamed: D17.1 (K), Q17.3 (C)
unnamed: D17.2 (A), R40.2
unnamed: D18.1 (K), Q18.3 (C)
unnamed: D18.2 (A), R41.2
unnamed: D19.1 (K), Q19.3 (C)
unnamed: D19.2 (A), R42.2
unnamed: D20.1 (K), Q20.3 (C)
unnamed: D20.2 (A), R43.2
unnamed: D21.1 (K), Q21.3 (C)
unnamed: D21.2 (A), R44.2
unnamed: D22.1 (K), Q22.3 (C)
unnamed: D22.2 (A), R45.2
unnamed: D23.1 (K), Q23.3 (C)
unnamed: D23.2 (A), R46.2
unnamed: J1.1 (Data_1e0), R13.2, TP15.1
unnamed: J1.2 (Data_2e0), R12.2, TP14.1
unnamed: J1.3 (Data_1e1), R9.2, TP11.1
unnamed: J1.4 (Data_2e1), R8.2, TP10.1
unnamed: J1.5 (Data_1e2), R1.2, TP7.1
unnamed: J1.6 (Data_2e2), R6.2, TP6.1
unnamed: J1.7 (Data_1e3), R3.2, TP3.1
unnamed: J1.9 (Range_1e0), R36.2, TP32.1
unnamed: J1.10 (Range_2e0), R35.2, TP31.1
unnamed: J1.11 (Range_1e1), R33.2, TP28.1
unnamed: J1.13 (Polarity), R28.2, TP23.1
unnamed: J1.14 (+15V), J1.17 (+15V), J1.39 (+15V), TP16.1
unnamed: J1.15 (Sensitivity_1e0), R32.2, TP27.1
unnamed: J1.16 (Sensitivity_2e0), R31.2, TP26.1
unnamed: J1.18 (+3.6V), TP18.1
unnamed: J1.23 (Print_Cmd), R30.2, TP25.1
unnamed: J1.24 (Ref_Lo), TP20.1
unnamed: J1.25 (Ref_Hi), TP17.1
unnamed: J1.26 (Data_4e0), R11.2, TP13.1
unnamed: J1.27 (Data_8e0), R10.2, TP12.1
unnamed: J1.28 (Data_4e1), R2.2, TP9.1
unnamed: J1.29 (Data_8e1), R7.2, TP8.1
unnamed: J1.30 (Data_4e2), R5.2, TP5.1
unnamed: J1.31 (Data_8e2), R4.2, TP4.1
unnamed: J1.33 (Overload), R29.2, TP24.1
unnamed: J1.34 (Range_4e0), R27.2, TP30.1
unnamed: J1.35 (Range_8e0), R34.2, TP29.1
unnamed: J1.42 (-15V), TP19.1
unnamed: J1.44 (Hold1), SW2.1 (A), TP33.1
unnamed: J1.45 (Hold2), SW3.1 (A), TP34.1
unnamed: J1.46 (Trigger), SW1.1, TP22.1
unnamed: J1.51 (SHIELD), R48.1
unnamed: J1.52 (SHIELD), R47.1
unnamed: Q1.1 (B), R3.1
unnamed: Q2.1 (B), R4.1
unnamed: Q3.1 (B), R5.1
unnamed: Q4.1 (B), R6.1
unnamed: Q5.1 (B), R1.1
unnamed: Q6.1 (B), R7.1
unnamed: Q7.1 (B), R2.1
unnamed: Q8.1 (B), R8.1
unnamed: Q9.1 (B), R9.1
unnamed: Q10.1 (B), R10.1
unnamed: Q11.1 (B), R11.1
unnamed: Q12.1 (B), R12.1
unnamed: Q13.1 (B), R13.1
unnamed: Q14.1 (B), R28.1
unnamed: Q15.1 (B), R29.1
unnamed: Q16.1 (B), R30.1
unnamed: Q17.1 (B), R31.1
unnamed: Q18.1 (B), R32.1
unnamed: Q19.1 (B), R33.1
unnamed: Q20.1 (B), R34.1
unnamed: Q21.1 (B), R27.1
unnamed: Q22.1 (B), R35.1
unnamed: Q23.1 (B), R36.1

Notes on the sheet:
Vf = 2 V 1 mA -> 2.91 kOhm .5 mA -> 5.82 kOhm

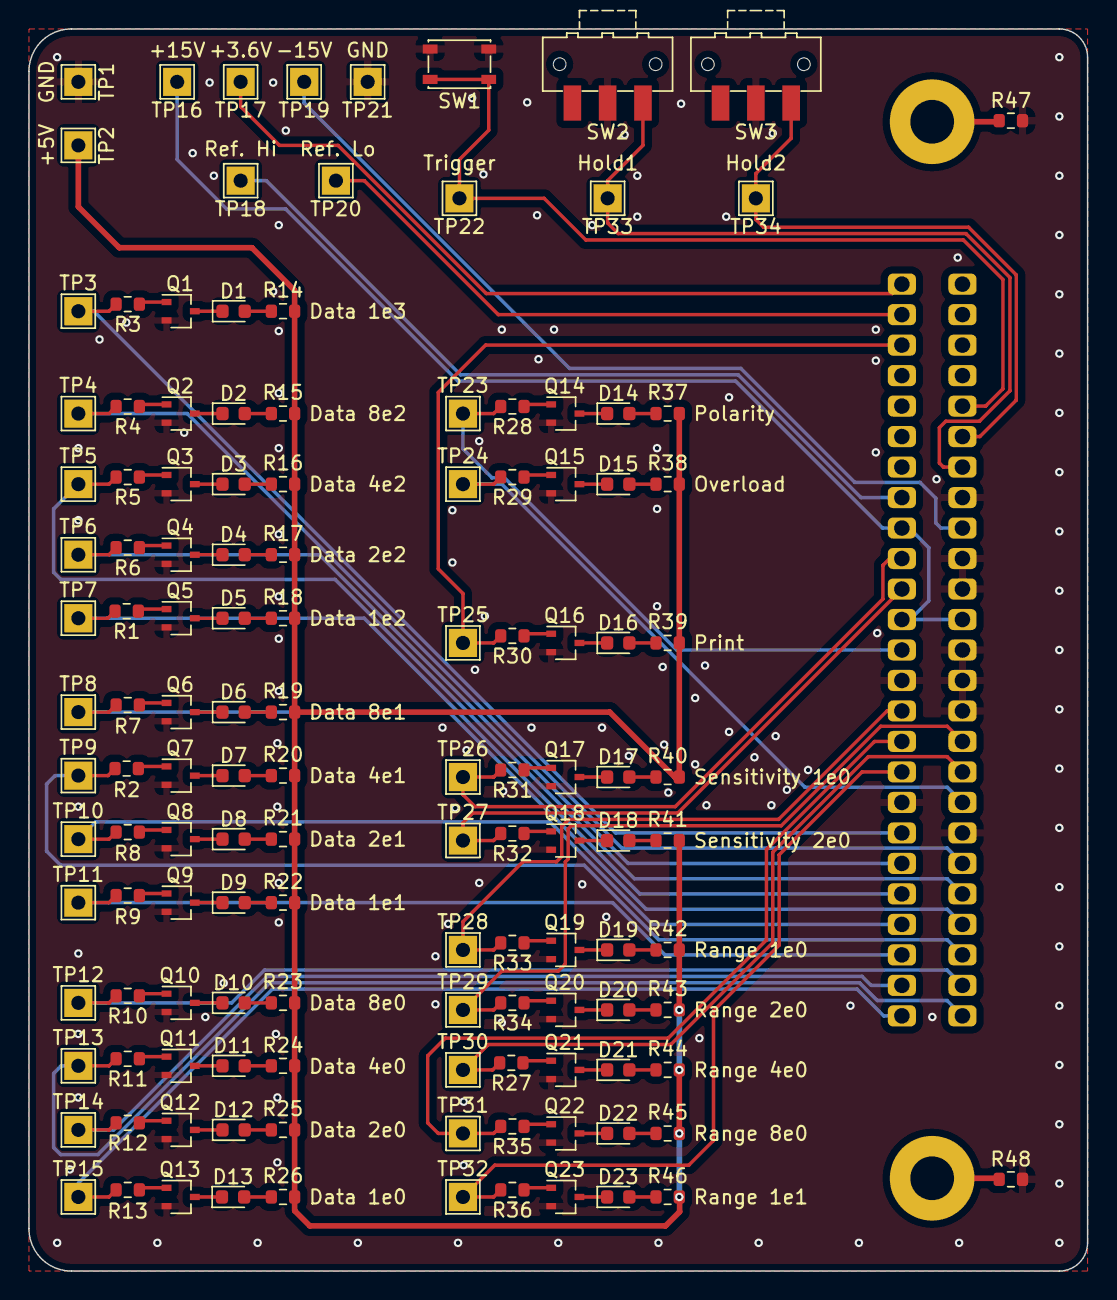
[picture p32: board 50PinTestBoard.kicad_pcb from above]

Board: 2 copper layers, 75.0 x 88.0 mm, 132 parts (1 on the bottom side), 104 nets.

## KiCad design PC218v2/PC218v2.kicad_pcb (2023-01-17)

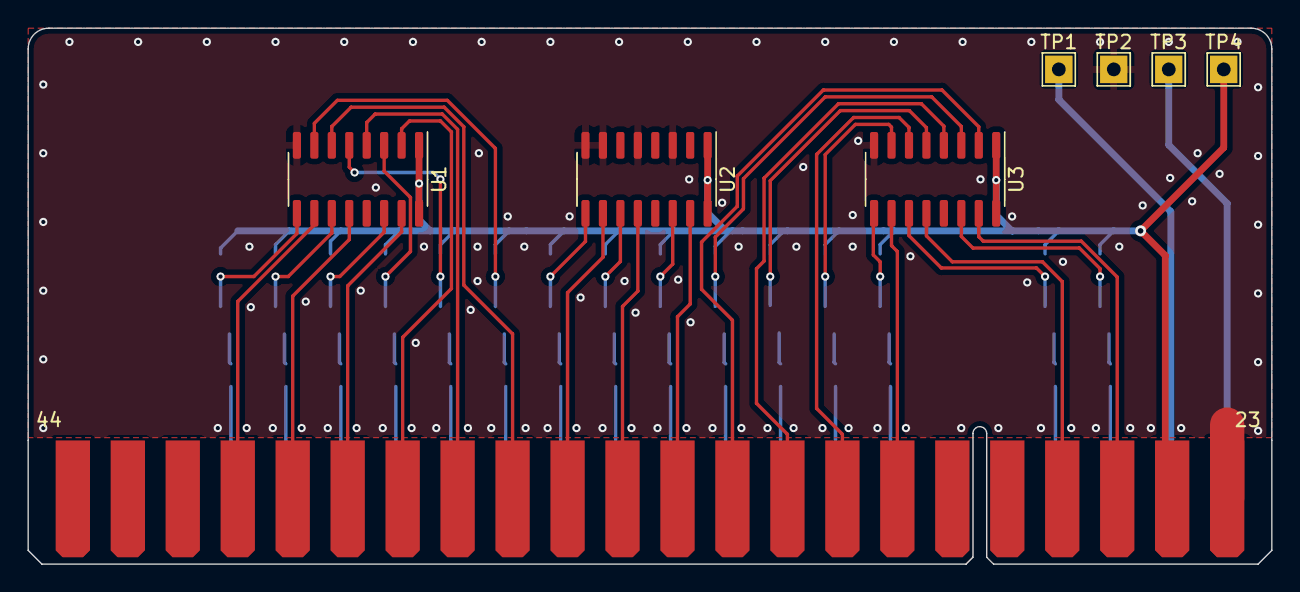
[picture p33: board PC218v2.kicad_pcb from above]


Board: 2 copper layers, 90.5 x 39.0 mm, 53 parts (45 on the bottom side), 64 nets.

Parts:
J1: PC218_BoardEdge_44pin; PC218_Edge_Connector
Q1, Q2, Q3, Q4, Q5, Q6, Q7, Q8, Q9, Q10, Q11, Q12, Q13, Q14, Q15: BC848W; SOT-323_SC-70
R1, R2, R3, R4, R5, R6, R7, R8, R9, R10, R11, R12, R13, R14, R15: 180K; R_0603_1608Metric
R16, R17, R18, R19, R20, R21, R22, R23, R24, R25, R26, R27, R28, R29, R30: 120K; R_0603_1608Metric
TP1: -15V; TestPoint_THTPad_2.0x2.0mm_Drill1.0mm
TP2: GND; TestPoint_THTPad_2.0x2.0mm_Drill1.0mm
TP3: 3.6V; TestPoint_THTPad_2.0x2.0mm_Drill1.0mm
TP4: 15V; TestPoint_THTPad_2.0x2.0mm_Drill1.0mm
U1, U2, U3: 4010; SOIC-16_3.9x9.9mm_P1.27mm

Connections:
1x10^0: J1.13 (1x10^0), R24.1
1x10^0 Print: J1.35 (1x10^0_Print), U2.10
1x10^1: J1.18 (1x10^1), R29.1
1x10^1 Print: J1.40 (1x10^1_Print), U1.12
1x10^2: J1.9 (1x10^2), R20.1
1x10^2 Print: J1.31 (1x10^2_Print), U3.4
1x10^3: J1.7 (1x10^3), R18.1
1x10^3 Print: J1.29 (1x10^3_Print), U3.10
2x10^0: J1.12 (2x10^0), R23.1
2x10^0 Print: J1.34 (2x10^0_Print), U2.12
2x10^1: J1.19 (2x10^1), R30.1
2x10^1 Print: J1.41 (2x10^1_Print), U1.10
2x10^2: J1.8 (2x10^2), R19.1
2x10^2 Print: J1.30 (2x10^2_Print), U3.6
4x10^0: J1.14 (4x10^0), R25.1
4x10^0 Print: J1.36 (4x10^0_Print), U1.6
4x10^1: J1.17 (4x10^1), R28.1
4x10^1 Print: J1.39 (4x10^1_Print), U1.15
4x10^2: J1.10 (4x10^2), R21.1
4x10^2 Print: J1.32 (4x10^2_Print), U3.2
8x10^0: J1.15 (8x10^0), R26.1
8x10^0 Print: J1.37 (8x10^0_Print), U1.4
8x10^1: J1.16 (8x10^1), R27.1
8x10^1 Print: J1.38 (8x10^1_Print), U1.2
8x10^2: J1.11 (8x10^2), R22.1
8x10^2 Print: J1.33 (8x10^2_Print), U2.15
+3.6V: J1.1 (3.6V), TP3.1
+15V: J1.24 (+15V), R1.1, R2.1, R3.1, R4.1, R5.1, R6.1, R7.1, R8.1, R9.1, R10.1, R11.1, R12.1, R13.1, R14.1, R15.1, TP4.1, U1.1 (VCC), U1.16 (VDD), U2.1 (VCC), U2.16 (VDD), U3.1 (VCC), U3.16 (VDD)
-15V: J1.2 (-15V), TP1.1
GND: J1.23 (GND), Q1.2 (E), Q2.2 (E), Q3.2 (E), Q4.2 (E), Q5.2 (E), Q6.2 (E), Q7.2 (E), Q8.2 (E), Q9.2 (E), Q10.2 (E), Q11.2 (E), Q12.2 (E), Q13.2 (E), Q14.2 (E), Q15.2 (E), TP2.1, U1.8 (VSS), U2.3, U2.5, U2.7, U2.8 (VSS), U3.8 (VSS)
unnamed: Q1.1 (B), R16.2
unnamed: Q1.3 (C), R1.2, U3.14
unnamed: Q2.1 (B), R17.2
unnamed: Q2.3 (C), R2.2, U3.11
unnamed: Q3.1 (B), R18.2
unnamed: Q3.3 (C), R3.2, U3.9
unnamed: Q4.1 (B), R19.2
unnamed: Q4.3 (C), R4.2, U3.7
unnamed: Q5.1 (B), R20.2
unnamed: Q5.3 (C), R5.2, U3.5
unnamed: Q6.1 (B), R21.2
unnamed: Q6.3 (C), R6.2, U3.3
unnamed: Q7.1 (B), R22.2
unnamed: Q7.3 (C), R7.2, U2.14
unnamed: Q8.1 (B), R23.2
unnamed: Q8.3 (C), R8.2, U2.11
unnamed: Q9.1 (B), R24.2
unnamed: Q9.3 (C), R9.2, U2.9
unnamed: Q10.1 (B), R25.2
unnamed: Q10.3 (C), R10.2, U1.7
unnamed: Q11.1 (B), R26.2
unnamed: Q11.3 (C), R11.2, U1.5
unnamed: Q12.1 (B), R27.2
unnamed: Q12.3 (C), R12.2, U1.3
unnamed: Q13.1 (B), R28.2
unnamed: Q13.3 (C), R13.2, U1.14
unnamed: Q14.1 (B), R29.2
unnamed: Q14.3 (C), R14.2, U1.11
unnamed: Q15.1 (B), R30.2
unnamed: Q15.3 (C), R15.2, U1.9
Overload: J1.4 (Overload), R17.1
Overload Print: J1.26 (Overload_Print), U3.12
Polarity: J1.3 (Polarity), R16.1
Polarity Print: J1.25 (Polarity_Print), U3.15

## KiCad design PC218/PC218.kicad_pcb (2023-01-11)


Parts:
J1: PC218_BoardEdge_44pin; PC218_Edge_Connector
Q1, Q2, Q3, Q4, Q5, Q6, Q7, Q8, Q9, Q10, Q11, Q12, Q13, Q14, Q15, Q16, Q17, Q18, Q19, Q20, Q21, Q22, Q23, Q24, Q25, Q26, Q27, Q28, Q29, Q30, Q31, Q32, Q33, Q34, Q35, Q36, Q37, Q38, Q39, Q40, Q41, Q42, Q43, Q44, Q45: BC848W; SOT-323_SC-70
R1, R5, R9, R13, R17, R19, R25, R29, R33, R37, R41, R45, R49, R53, R57: 120K; R_0603_1608Metric
R2, R6, R10, R14, R18, R20, R26, R30, R34, R38, R42, R46, R50, R54, R58: 10K; R_0603_1608Metric
R3, R7, R11, R15, R21, R22, R27, R31, R35, R39, R43, R47, R51, R55, R59: 180K; R_0603_1608Metric
R4, R8, R12, R16, R23, R24, R28, R32, R36, R40, R44, R48, R52, R56, R60: 3.9K; R_0603_1608Metric

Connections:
1x10^0: J1.13 (1x10^0), R45.1, R46.1
1x10^0 Print: J1.35 (1x10^0_Print), Q35.2 (E), Q36.3 (C)
1x10^1: J1.18 (1x10^1), R29.1, R30.1
1x10^1 Print: J1.40 (1x10^1_Print), Q23.2 (E), Q24.3 (C)
1x10^2: J1.9 (1x10^2), R9.1, R10.1
1x10^2 Print: J1.31 (1x10^2_Print), Q8.2 (E), Q9.3 (C)
1x10^3: J1.7 (1x10^3), R19.1, R20.1
1x10^3 Print: J1.29 (1x10^3_Print), Q17.2 (E), Q18.3 (C)
2x10^0: J1.12 (2x10^0), R49.1, R50.1
2x10^0 Print: J1.34 (2x10^0_Print), Q38.2 (E), Q39.3 (C)
2x10^1: J1.19 (2x10^1), R33.1, R34.1
2x10^1 Print: J1.41 (2x10^1_Print), Q26.2 (E), Q27.3 (C)
2x10^2: J1.8 (2x10^2), R13.1, R14.1
2x10^2 Print: J1.30 (2x10^2_Print), Q11.2 (E), Q12.3 (C)
4x10^0: J1.14 (4x10^0), R53.1, R54.1
4x10^0 Print: J1.36 (4x10^0_Print), Q41.2 (E), Q42.3 (C)
4x10^1: J1.17 (4x10^1), R37.1, R38.1
4x10^1 Print: J1.39 (4x10^1_Print), Q29.2 (E), Q30.3 (C)
4x10^2: J1.10 (4x10^2), R17.1, R18.1
4x10^2 Print: J1.32 (4x10^2_Print), Q15.2 (E), Q16.3 (C)
8x10^0: J1.15 (8x10^0), R57.1, R58.1
8x10^0 Print: J1.37 (8x10^0_Print), Q44.2 (E), Q45.3 (C)
8x10^1: J1.16 (8x10^1), R41.1, R42.1
8x10^1 Print: J1.38 (8x10^1_Print), Q32.2 (E), Q33.3 (C)
8x10^2: J1.11 (8x10^2), R25.1, R26.1
8x10^2 Print: J1.33 (8x10^2_Print), Q20.2 (E), Q21.3 (C)
+15V: J1.24 (+15V), R3.1, R4.1, R7.1, R8.1, R11.1, R12.1, R15.1, R16.1, R21.1, R22.1, R23.1, R24.1, R27.1, R28.1, R31.1, R32.1, R35.1, R36.1, R39.1, R40.1, R43.1, R44.1, R47.1, R48.1, R51.1, R52.1, R55.1, R56.1, R59.1, R60.1
-15V: J1.2 (-15V)
GND: J1.23 (GND), Q1.2 (E), Q3.2 (E), Q4.2 (E), Q6.2 (E), Q7.2 (E), Q9.2 (E), Q10.2 (E), Q12.2 (E), Q13.2 (E), Q14.2 (E), Q16.2 (E), Q18.2 (E), Q19.2 (E), Q21.2 (E), Q22.2 (E), Q24.2 (E), Q25.2 (E), Q27.2 (E), Q28.2 (E), Q30.2 (E), Q31.2 (E), Q33.2 (E), Q34.2 (E), Q36.2 (E), Q37.2 (E), Q39.2 (E), Q40.2 (E), Q42.2 (E), Q43.2 (E), Q45.2 (E)
unnamed: Q1.1 (B), R1.2
unnamed: Q1.3 (C), Q2.1 (B), R3.2
unnamed: Q2.3 (C), R4.2
unnamed: Q3.1 (B), R2.2
unnamed: Q4.1 (B), R5.2
unnamed: Q4.3 (C), Q5.1 (B), R7.2
unnamed: Q5.3 (C), R8.2
unnamed: Q6.1 (B), R6.2
unnamed: Q7.1 (B), R9.2
unnamed: Q7.3 (C), Q8.1 (B), R11.2
unnamed: Q8.3 (C), R12.2
unnamed: Q9.1 (B), R10.2
unnamed: Q10.1 (B), R13.2
unnamed: Q10.3 (C), Q11.1 (B), R15.2
unnamed: Q11.3 (C), R16.2
unnamed: Q12.1 (B), R14.2
unnamed: Q13.1 (B), R17.2
unnamed: Q13.3 (C), Q15.1 (B), R21.2
unnamed: Q14.1 (B), R19.2
unnamed: Q14.3 (C), Q17.1 (B), R22.2
unnamed: Q15.3 (C), R23.2
unnamed: Q16.1 (B), R18.2
unnamed: Q17.3 (C), R24.2
unnamed: Q18.1 (B), R20.2
unnamed: Q19.1 (B), R25.2
unnamed: Q19.3 (C), Q20.1 (B), R27.2
unnamed: Q20.3 (C), R28.2
unnamed: Q21.1 (B), R26.2
unnamed: Q22.1 (B), R29.2
unnamed: Q22.3 (C), Q23.1 (B), R31.2
unnamed: Q23.3 (C), R32.2
unnamed: Q24.1 (B), R30.2
unnamed: Q25.1 (B), R33.2
unnamed: Q25.3 (C), Q26.1 (B), R35.2
unnamed: Q26.3 (C), R36.2
unnamed: Q27.1 (B), R34.2
unnamed: Q28.1 (B), R37.2
unnamed: Q28.3 (C), Q29.1 (B), R39.2
unnamed: Q29.3 (C), R40.2
unnamed: Q30.1 (B), R38.2
unnamed: Q31.1 (B), R41.2
unnamed: Q31.3 (C), Q32.1 (B), R43.2
unnamed: Q32.3 (C), R44.2
unnamed: Q33.1 (B), R42.2
unnamed: Q34.1 (B), R45.2
unnamed: Q34.3 (C), Q35.1 (B), R47.2
unnamed: Q35.3 (C), R48.2
unnamed: Q36.1 (B), R46.2
unnamed: Q37.1 (B), R49.2
unnamed: Q37.3 (C), Q38.1 (B), R51.2
unnamed: Q38.3 (C), R52.2
unnamed: Q39.1 (B), R50.2
unnamed: Q40.1 (B), R53.2
unnamed: Q40.3 (C), Q41.1 (B), R55.2
unnamed: Q41.3 (C), R56.2
unnamed: Q42.1 (B), R54.2
unnamed: Q43.1 (B), R57.2
unnamed: Q43.3 (C), Q44.1 (B), R59.2
unnamed: Q44.3 (C), R60.2
unnamed: Q45.1 (B), R58.2
Overload: J1.4 (Overload), R5.1, R6.1
Overload Print: J1.26 (Overload_Print), Q5.2 (E), Q6.3 (C)
Polarity: J1.3 (Polarity), R1.1, R2.1
Polarity Print: J1.25 (Polarity_Print), Q2.2 (E), Q3.3 (C)


Board: 2 copper layers, 107.0 x 48.0 mm, 106 parts (0 on the bottom side), 92 nets.

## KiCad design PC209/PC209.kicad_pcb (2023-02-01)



Board: 2 copper layers, 90.5 x 39.0 mm, 79 parts (52 on the bottom side), 68 nets.

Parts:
C1, C5: 1 nF; C_0603_1608Metric
C2: 100 pF; C_0603_1608Metric
C3: 100 nF; C_0603_1608Metric
C4: 3.3 nF; C_0603_1608Metric
C6, C7: 470 pF; C_0603_1608Metric
J1: PC209_BoardEdge_44pin; PC209_Edge_Connector
Q1, Q2, Q3, Q4, Q5, Q6, Q7, Q8, Q9, Q10, Q11, Q12, Q13, Q14, Q15, Q16, Q17: BC848W; SOT-323_SC-70
R1, R3, R4, R5, R6, R7, R8, R19, R32: 180k; R_0603_1608Metric
R2, R28, R45: 1k; R_0603_1608Metric
R9, R24, R25, R26, R27: 634; R_0603_1608Metric
R10, R12, R13, R14, R15, R16, R17, R18, R31, R35: 120k; R_0603_1608Metric
R11, R20, R21, R29, R30, R33, R34: 453; R_0603_1608Metric
R22, R23: 3.3k; R_0603_1608Metric
R36, R37, R38, R39, R40, R41: 0; R_0603_1608Metric
R42: 6.98k; R_0603_1608Metric
R43: 6.04k; R_0603_1608Metric
R44: 2k; R_0603_1608Metric
TP1: GND; TestPoint_THTPad_2.0x2.0mm_Drill1.0mm
TP2: 3.6 V; TestPoint_THTPad_2.0x2.0mm_Drill1.0mm
TP3: 15 V; TestPoint_THTPad_2.0x2.0mm_Drill1.0mm
TP4: 100 μs pulse; TestPoint_THTPad_2.0x2.0mm_Drill1.0mm
TP5: 10 μs delay; TestPoint_THTPad_2.0x2.0mm_Drill1.0mm
TP6: ~Sample; TestPoint_THTPad_2.0x2.0mm_Drill1.0mm
TP7: Sample; TestPoint_THTPad_2.0x2.0mm_Drill1.0mm
U1, U2: 4010; SOIC-16_3.9x9.9mm_P1.27mm

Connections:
1e-2 Range: J1.29 (1e-2_Range), R39.2
+3.6V: J1.23 (+3.6V), R9.2, R22.2, R23.2, R24.2, R25.2, R26.2, R27.2, TP2.1
+15V: J1.2 (+15V), R1.2, R3.2, R4.2, R5.2, R6.2, R7.2, R8.2, R19.2, R32.1, R42.1, TP3.1, U1.1 (VCC), U1.16 (VDD), U2.1 (VCC), U2.16 (VDD)
/Pulse Generator/Output: C2.1, C3.1, C6.2, Q13.3 (C), Q14.3 (C), R18.1, R24.1, R35.1, TP4.1
Buffer Storage: J1.43 (Buffer_Storage), R11.1, TP7.1
GND: J1.1 (GND), Q1.2 (E), Q2.2 (E), Q3.2 (E), Q4.2 (E), Q5.2 (E), Q6.2 (E), Q7.2 (E), Q8.2 (E), Q9.2 (E), Q10.2 (E), Q11.2 (E), Q12.2 (E), Q13.2 (E), Q14.2 (E), Q15.2 (E), Q16.2 (E), Q17.2 (E), R2.1, R28.1, R44.2, R45.1, TP1.1, U1.8 (VSS), U2.8 (VSS), U2.9, U2.11, U2.14
High Reference: J1.11 (High_Reference), R42.2, R43.1
Hold 1: J1.27 (Hold_1), R38.2
Hold 1 Out: J1.5 (Hold_1_Out), R38.1
Hold 2: J1.26 (Hold_2), R37.2
Hold 2 Out: J1.4 (Hold_2_Out), R37.1
Low Reference: J1.12 (Low_Reference), R43.2, R44.1
unnamed: C1.1, Q2.3 (C), R9.1
unnamed: C1.2, R2.2, R34.1, TP6.1
unnamed: C2.2, Q9.1 (B), R18.2
unnamed: C3.2, R21.1, R22.1
unnamed: C4.1, C5.1, C7.2, Q12.3 (C), Q15.3 (C), R25.1, TP5.1
unnamed: C4.2, R20.1, R23.1
unnamed: C5.2, R28.2, R33.1
unnamed: C6.1, Q10.3 (C), R26.1, R30.2
unnamed: C7.1, Q11.3 (C), R27.1, R29.2
unnamed: Q1.1 (B), R10.2
unnamed: Q1.3 (C), R1.1, R31.1, U2.7
unnamed: Q2.1 (B), R11.2
unnamed: Q3.1 (B), R12.2
unnamed: Q3.3 (C), R3.1, U1.11
unnamed: Q4.1 (B), R13.2
unnamed: Q4.3 (C), R4.1, U1.9
unnamed: Q5.1 (B), R14.2
unnamed: Q5.3 (C), R5.1, U1.7
unnamed: Q6.1 (B), R15.2
unnamed: Q6.3 (C), R6.1, U1.5
unnamed: Q7.1 (B), R16.2
unnamed: Q7.3 (C), R7.1, U1.3
unnamed: Q8.1 (B), R17.2
unnamed: Q8.3 (C), R8.1, U1.14
unnamed: Q9.3 (C), R19.1, U2.3
unnamed: Q10.1 (B), R21.2
unnamed: Q11.1 (B), R20.2
unnamed: Q12.1 (B), R29.1
unnamed: Q13.1 (B), R30.1
unnamed: Q14.1 (B), R33.2
unnamed: Q15.1 (B), R34.2
unnamed: Q16.1 (B), R31.2
unnamed: Q16.3 (C), Q17.3 (C), R32.2, U2.5
unnamed: Q17.1 (B), R35.2
Print CMD A: J1.20 (Print_CMD_A), U2.2
Print CMD B: J1.21 (Print_CMD_B), U2.4
Range 1: J1.41 (Range_1), R12.1
Range 1 Print: J1.19 (Range_1_Print), U1.12
Range 1e-2 Out: J1.7 (Range_1e-2_Out), R39.1
Range 2: J1.40 (Range_2), R13.1
Range 2 Print: J1.18 (Range_2_Print), U1.10
Range 4: J1.39 (Range_4), R14.1
Range 4 Print: J1.17 (Range_4_Print), U1.6
Range 8: J1.38 (Range_8), R15.1
Range 8 Print: J1.16 (Range_8_Print), U1.4
Range 10: J1.37 (Range_10), R16.1
Range 10 Print: J1.15 (Range_10_Print), U1.2
Range Hold: J1.30 (Range_Hold), R40.2
Range Hold Out: J1.8 (Range_Hold_Out), R40.1
Range Signal: J1.44 (Range_Signal), R10.1, R45.2
Range Signal Print: J1.22 (Range_Signal_Print), U2.6
Trigger: J1.25 (Trigger), R36.2
Trigger Out: J1.3 (Trigger_Out), R36.1
Zero Check: J1.36 (Zero_Check), R17.1, R41.2
Zero Check Out: J1.9 (Zero_Check_Out), R41.1
Zero Check Print: J1.14 (Zero_Check_Print), U1.15

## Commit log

2022-12-30 Initial prototype for PC218
    [PC218.kicad_pcb, PC218.kicad_sch]
2022-12-31 Add new version of PC218 using less components.
    [PC218.csv, PC218.kicad_pcb, PC218.kicad_sch]
2023-01-11 Add images of boards, update README, add LICENSE
2023-01-11 PC218 Rev 1.1
    Fixed disconnected ground plane resulting in two buffers being unpowered
    Moved silkscreen to front, add OSHW logo
    Move symbols and footprints to shared library
    Update edge connector footprint to use a more sane orientation
    [PC218.csv, PC218.kicad_pcb, PC218.kicad_sch]
2023-01-11 Rename project files for PC218 Rev 2
    [PC218v2.kicad_pcb, PC218v2.kicad_sch]
2023-01-11 PC218 Rev 2.1
    [PC218v2.kicad_pcb, PC218v2.kicad_sch]
2023-01-12 PC209: Initial design for pulse generator
    [PC209.kicad_pcb, PC209.kicad_sch, pulse_generator.kicad_sch]
2023-01-16 PC209: Initial layout for pulse generator sections
    [PC209.kicad_pcb, PC209.kicad_sch, pulse_generator.kicad_sch]
2023-01-16 PC209: Initial board routing
    [PC209.kicad_pcb, PC209.kicad_sch]
2023-01-16 PC209: Rev 1.0
    [PC209.kicad_pcb, PC209.kicad_sch, pulse_generator.kicad_sch]
2023-01-17 PC218v2: Rev 2.2
    Matched form factor of new PC209 board
    Added power test points
    [PC218v2.kicad_pcb, PC218v2.kicad_sch]
2023-01-17 PC209: Fix silkscreen error, backannotate to schematic.
    [PC209.kicad_pcb, PC209.kicad_sch, pulse_generator.kicad_sch]
2023-01-18 50PinTestBoard: Start work on board to test all connections of the 50-pin connector.
    [50PinTestBoard.kicad_pcb, 50PinTestBoard.kicad_sch]
2023-01-19 50PinTestBoard: Rev 1.0
    [50PinTestBoard.kicad_pcb, 50PinTestBoard.kicad_sch]
2023-01-21 50PinTestBoard: Rev 1.1
    Made screw holes for connector foot print plated through-holes.
    [50PinTestBoard.kicad_pcb, 50PinTestBoard.kicad_sch]
2023-01-25 InterfaceBoard: Rough in Ethernet, USB, and 50-pin
    [50pin.kicad_sch, InterfaceBoard.kicad_pcb, InterfaceBoard.kicad_sch, MCU.kicad_sch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]
2023-01-25 Add PDFs of schematics and board layout.
2023-01-26 InterfaceBoard: Add RS-232/DE-9
    [InterfaceBoard.kicad_pcb, InterfaceBoard.kicad_sch, MCU.kicad_sch, RS232.kicad_sch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]
2023-01-28 InterfaceBoard: Add STM32G0B1RET
    [InterfaceBoard.kicad_pcb, InterfaceBoard.kicad_sch, MCU.kicad_sch, USB.kicad_sch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]
2023-02-01 PC209: Fix position of -15 V and +3.6 V on card edge
    Update component values
    Make library path relative
    [PC209.kicad_pcb, PC209.kicad_sch, pulse_generator.kicad_sch]
2023-02-01 InterfaceBoard: Make library paths relative
    [InterfaceBoard.kicad_pcb, InterfaceBoard.kicad_sch, MCU.kicad_sch, USB.kicad_sch]
2023-02-01 PC209: Add simulation document
    [pc209.sch]
2023-02-01 PC209: Add BOM
    [PC209.csv, PC209.kicad_sch, pulse_generator.kicad_sch]
2023-02-04 50PinTestBoard: Fix year
    [50PinTestBoard.kicad_pcb]
2023-02-05 Fix 50-pin connector pin numbering.
2023-02-05 50PinTestBoard: Rev 1.2
    Fix orientation of connector footprint
    - Moved connector to bottom of board to avoid re-routing entire board.
    Update resistor value(s).
    Add Digi-Key links for parts.
    [50PinTestBoard.kicad_pcb, 50PinTestBoard.kicad_sch]
2023-02-05 50PinTestBoard: Add BOM
    [50PinTestBoard.csv]
2023-02-05 InterfaceBoard: Update connector footprint
    [InterfaceBoard.kicad_pcb, InterfaceBoard.kicad_sch, MCU.kicad_sch]
2023-02-22 InterfaceBoard: Add 3.3 V regulater, test points.
    [InterfaceBoard.kicad_pcb, InterfaceBoard.kicad_sch, MCU.kicad_sch, PowerSupply.kicad_sch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]
2023-02-22 InterfaceBoard: MAX232 -> MAX3232
    [InterfaceBoard.kicad_pcb, InterfaceBoard.kicad_sch, RS232.kicad_sch]
2023-02-24 InterfaceBoard: Routed Ethernet
    [InterfaceBoard.kicad_pcb, InterfaceBoard.kicad_sch, RS232.kicad_sch]
2023-02-26 InterfaceBoard: Routed some digital interfaces to MCU
    [InterfaceBoard.kicad_pcb, InterfaceBoard.kicad_sch, MCU.kicad_sch, PowerSupply.kicad_sch]
2023-03-01 InterfaceBoard: Place and route buttons and LEDs.
    [InterfaceBoard.kicad_pcb, InterfaceBoard.kicad_sch, MCU.kicad_sch, USB.kicad_sch]
2023-03-01 InterfaceBoard: Swap trigger and reset buttons
    [InterfaceBoard.kicad_pcb]
2023-03-02 InterfaceBoard: Route MCU USB
    [InterfaceBoard.kicad_pcb, InterfaceBoard.kicad_sch, USB.kicad_sch]
2023-03-03 InterfaceBoard: Fully route board.
    [InterfaceBoard.kicad_pcb]
2023-03-03 InterfaceBoard: Geographical reannotation.
    [InterfaceBoard.kicad_pcb]
2023-03-04 InterfaceBoard: Rev 1.0
    [50pin.kicad_sch, InterfaceBoard.kicad_pcb, InterfaceBoard.kicad_sch, MCU.kicad_sch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]
2023-03-04 InterfaceBoard: Add BOM
    [50pin.kicad_sch, InterfaceBoard.csv, InterfaceBoard.kicad_sch, MCU.kicad_sch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]
2023-03-04 InterfaceBoard: Add PCB/SCH PDFs.
    [InterfaceBoard.kicad_pcb]
2023-03-31 Update board images
2023-11-03 DNI R31 from PC209
    This resistor prevents sensitivity 2x10^0 from hitting the proper logic levels.
    [PC209.kicad_sch, pulse_generator.kicad_sch]
